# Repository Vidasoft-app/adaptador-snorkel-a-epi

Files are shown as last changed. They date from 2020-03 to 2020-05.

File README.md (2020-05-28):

# Adaptador máscara Snorkel a EPIs y CPAP

Ver en [Español](https://github.com/Vidasoft-app/mascaras-3d-coronavirus-protocas3d/blob/master/README.md), [English](https://github.com/Vidasoft-app/mascaras-3d-coronavirus-protocas3d/blob/master/README-en-gb.md).

[Entra en la página web oficial](https://coronavirus.vidasoft.es)

Proyecto de código abierto, libre para uso de la emergencia sanitaria.

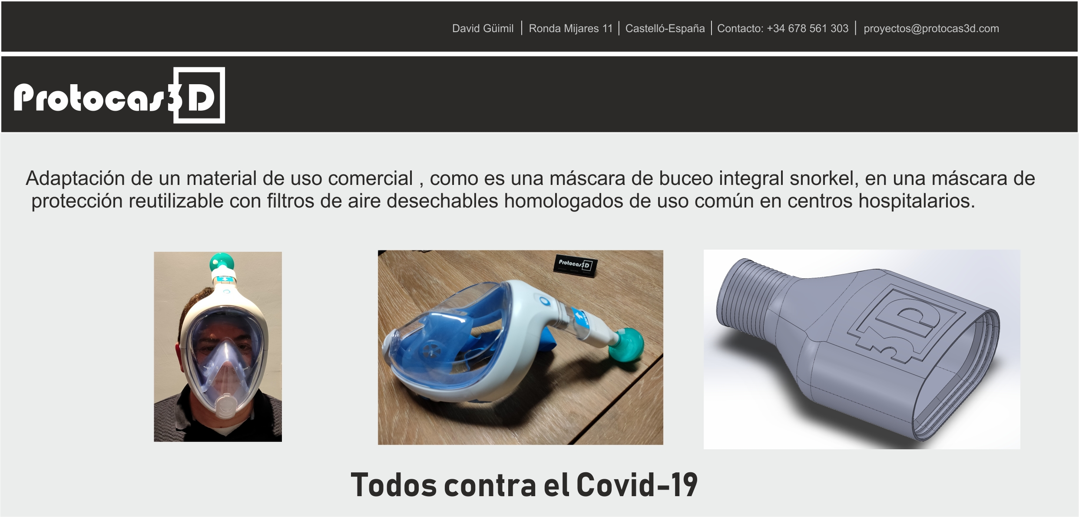
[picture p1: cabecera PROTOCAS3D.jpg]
imagen explicativa adaptación máscara buceo snorkel a EPIs sanitario


## ¿De que trata este proyecto?

Se trata de un adaptador para hacer compatible las máscaras de [snorkel](https://es.wikipedia.org/wiki/Esn%C3%B3rquel) con el filtro respiratorio hospitalario de forma que puedas usar la máscara de Snorkel de 2 maneras:

1. EPIs sanitario. Protección individual más completa y aislante.
2. Máscara para respirador (con CPAP) para uso no invasivo.

Estas piezas para EPIs o CPAP se puede crear mediante impresión 3D o mediante mecanizado industrial. 

Por otro lado, también se incluye para impresión 3D el emboltorio del "insumo desechable con filtro HEPA-H13" pero modificado para ser reutilizable. Sabemos que hay sitios dónde estos insumos desechables son un problema y tener esa pieza reutilizable puede ayudar.

Este adaptador te permite con unos sencillos pasos (más abajo) hacer que estas máscaras pueda ayudar como EPIs.

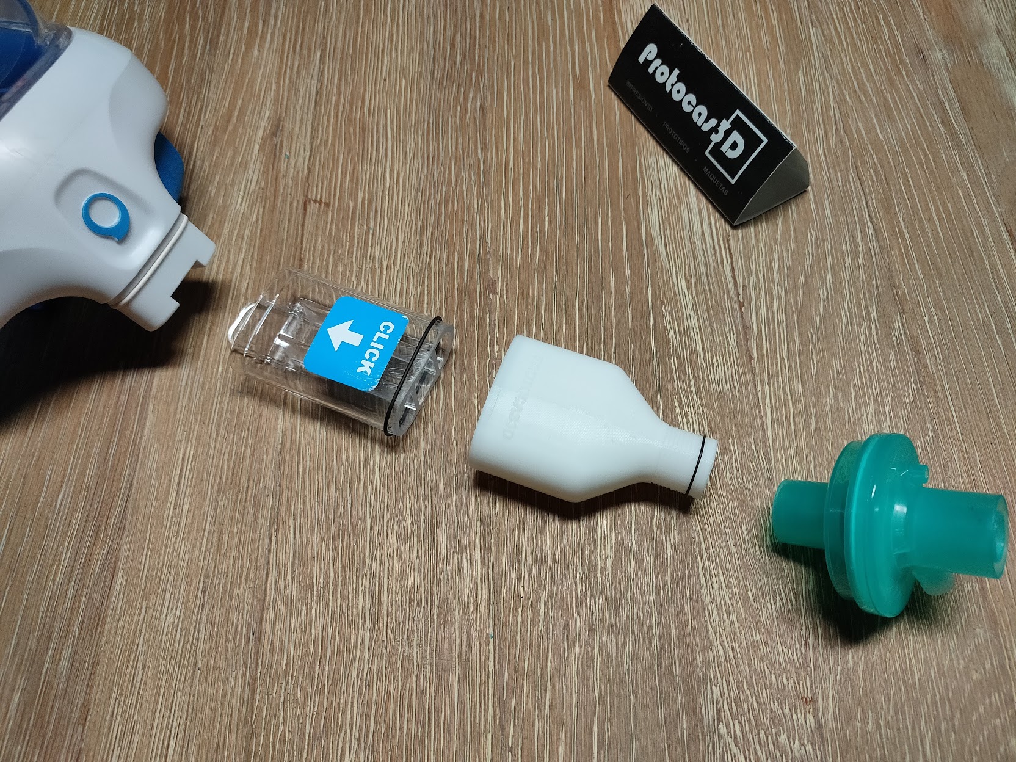
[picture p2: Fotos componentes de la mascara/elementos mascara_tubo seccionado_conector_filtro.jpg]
Máscara snorkel adaptada para ser EPI

Versión protección EPIs.

## Requisitos de impresión

* Impresión sin soportes.
* Extrusor 0,4 (que es el estándar)
* Temperatura extrusor 210
* Cama 50
* Material PLA (es el que utilizamos nosotros)

## Máscaras compatibles

* https://www.pccomponentes.com/ksix-mascara-snorkel-para-go-pro-y-camaras-deportivas
* https://www.decathlon.es/es/p/mascara-snorkel-ensuperficie-easybreath-500-oyster/_/R-p-148873?mc=8491269&c=VERDE_AZUL+TURQUESA
* https://www.decathlon.es/es/p/mascara-de-snorkel-en-superficie-easybreath-azul/_/R-p-1616?mc=8526111&c=AZUL_AZUL+TURQUESA

## Enlaces directos a las piezas

* Adaptador EPIs protección individual: 
  * Versión impresión 3D: [Enlace a las marcas de máscaras compatibles](https://github.com/Vidasoft-app/adaptador-snorkel-a-epi/tree/master/M%C3%A1scara%20snorkel%20a%20EPI_IMPRESI%C3%93N%203D)
  * Versión Mecanizado: [Enlace a los ficheros](https://github.com/Vidasoft-app/adaptador-snorkel-a-epi/tree/master/M%C3%A1scara%20snorkel%20a%20EPI_MECANIZADO/m%C3%A1scara%20Decathlon)
* Adaptador CPAP respirador no invasivo:
  * Versión impresión 3D: [Enlace a las marcas de máscaras compatibles](https://github.com/Vidasoft-app/adaptador-snorkel-a-epi/tree/master/Mascara%20snorkel%20a%20CPAP_IMPRESI%C3%93N%203D)
  * Versión Mecanizado: [Enlace a los ficheros](https://github.com/Vidasoft-app/adaptador-snorkel-a-epi/tree/master/M%C3%A1scara%20snorkel%20a%20CPAP_MECANIZADO)
* Emboltorio filtro HEPA-H13: [Enlace a los ficheros]()
  * Versión impresión 3D: [Enlace a los ficheros](https://github.com/Vidasoft-app/adaptador-snorkel-a-epi/tree/master/Filtro%20re-utilizable%20para%20EPI%20(PPE)_)

### ¿El adaptador no es compatible con tu máscara?

Tienes las fuentes disponibles [pulsando aquí](https://github.com/Vidasoft-app/adaptador-snorkel-a-epi/tree/master/Archivos%203D%20editables%20conector%20a%20filtro%20Version%204) para que puedas adaptarlo a tus necesidades estes dónde estes.

Código libre, ya sabes :)

## Proceso de adaptación

Los pasos son: 
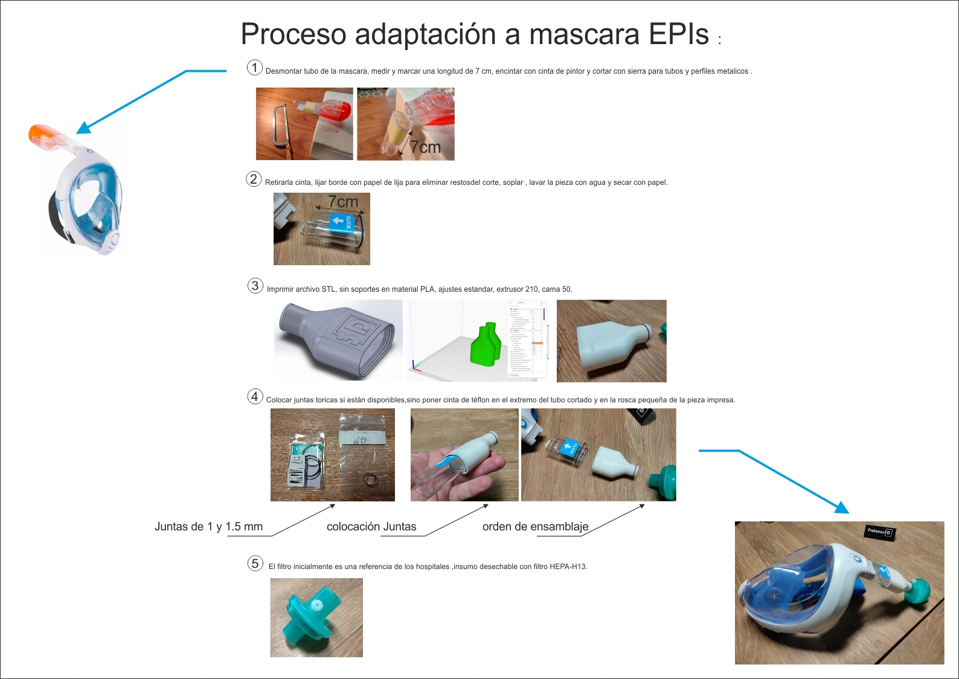
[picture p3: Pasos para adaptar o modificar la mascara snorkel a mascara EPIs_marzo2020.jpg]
Proceso de adaptación


También te los puedes descargar en PDF [pulsando en este enlace](https://github.com/Vidasoft-app/mascaras-3d-coronavirus-protocas3d/blob/master/Pasos%20para%20adaptar%20o%20modificar%20la%20mascara%20snorkel%20a%20mascara%20EPIs_marzo2020.pdf)

## ¿Como ponerse la máscara correctamente?

Te lo explicamos en [este vídeo](https://www.youtube.com/watch?v=PjzaguY-Ay0)

## ¿Tenemos licencia para tener este proyecto de código libre?

Si. El proyecto parte de unos médicos Colombianos los cuales nos han dado licencia explicita para compartir.

## ¿Tienes dudas? puedes preguntarnos directamente.

Puedes ponerte en contacto con todo el equipo del proyecto mediante el correo de:

coronavirus@vidasoft.es

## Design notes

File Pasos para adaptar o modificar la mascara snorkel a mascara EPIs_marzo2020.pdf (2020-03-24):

# Proceso adaptación a mascara EPIs :

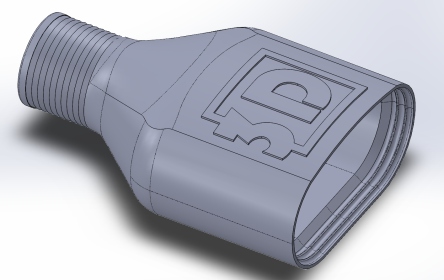
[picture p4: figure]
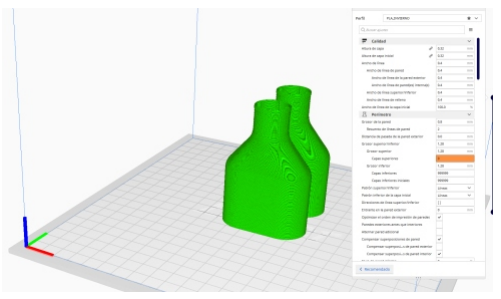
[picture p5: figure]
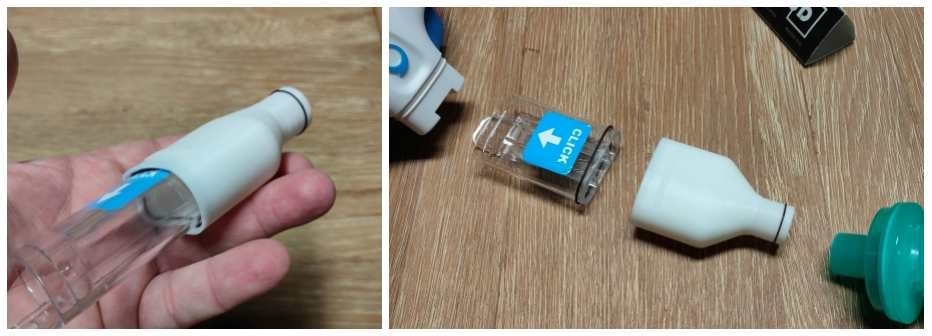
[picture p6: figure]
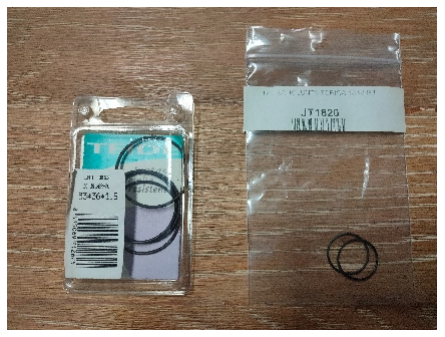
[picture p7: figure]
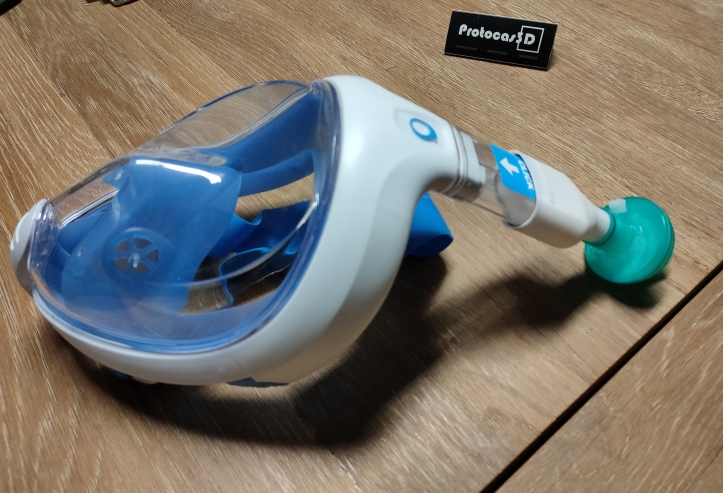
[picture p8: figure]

Juntas de 1 y 1.5 mm | colocación Juntas | orden de ensamblaje

Desmontar tubo de la mascara, medir y marcar una longitud de 7 cm, encintar con cinta de pintor y cortar con sierra para tubos y perfiles metalicos .

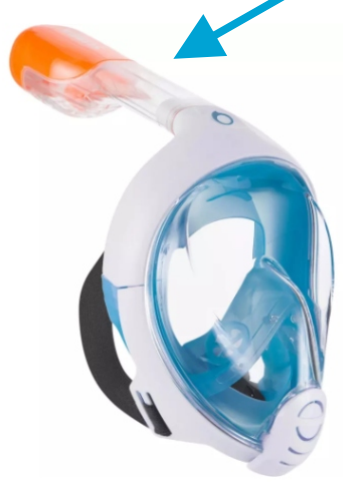
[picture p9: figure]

Retirarla cinta, lijar borde con papel de lija para eliminar restosdel corte, soplar , lavar la pieza con agua y secar con papel.

Imprimir archivo STL, sin soportes en material PLA, ajustes estandar, extrusor 210, cama 50.

Colocar juntas toricas si están disponibles,sino poner cinta de téflon en el extremo del tubo cortado y en la rosca pequeña de la pieza impresa.

El filtro inicialmente es una referencia de los hospitales ,insumo desechable con filtro HEPA-H13.

1

2

3

4

5

7cm

7cm

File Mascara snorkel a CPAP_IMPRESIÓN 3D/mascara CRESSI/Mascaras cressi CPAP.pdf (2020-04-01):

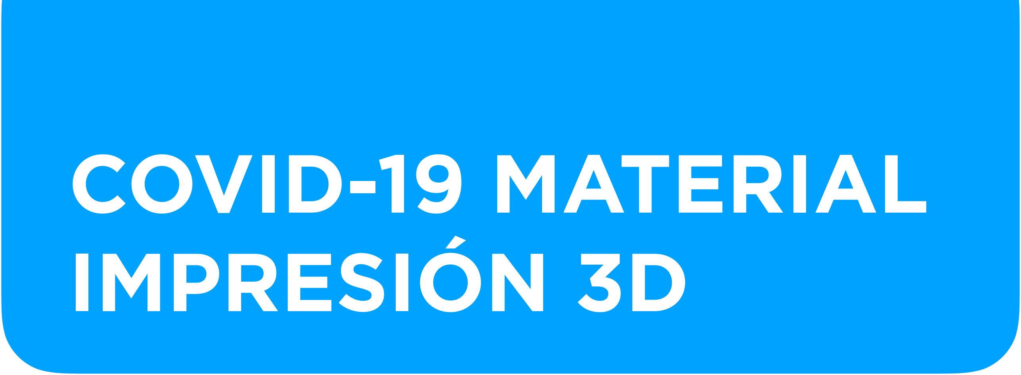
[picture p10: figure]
COVID-19 MATERIAL IMPRESIÓN 3D

# REFERENCIA: 3DPT021

USO

Adaptación de la máscara Duke de Cressi® para su uso como sistema CPAP de Boussignac

NECESIDAD

Se prevé aumento de la necesidad en todos los hospitales, debido a la alta previsión de pacientes que requerirán sistemas de respiración no invasivos en el pico de la epidemia.

# PARTES

1 | 3DPT021-1
Adaptador de la máscara Duke de Cressi®

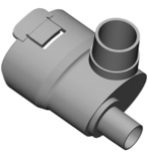
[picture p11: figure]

2 | 3DPT021-2

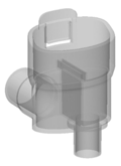
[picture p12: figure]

Soporte para válvula antiretorno

3 | 3DPT24

Opcional (en caso de no tener disponibilidad de filtro viricobacteriano)

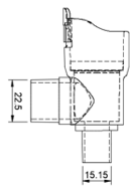
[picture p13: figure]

VALIDACIÓN CLINICA

- Máscara M/L i S/M Duke de Cressi®
- 3DPT021-1
- 3DPT021-2 ensamblada con la válvula

antirretorno de silicona extra, suministrada por el fabricante en el envase precintado de la misma máscara. En el interior de esta.

Resultados:

1. Con válvula antiretorno.
Se consiguieron presiones en el circuito a final de espiración de 10 cm H2O. No se observó la presencia de flujo retrógrado en todas las pruebas.

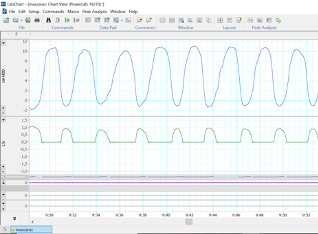
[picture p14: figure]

Resultados:

2. Sin Válvula antirretorno

Las presiones a final de espiración conseguidas alcanzaron 4 cm H2O (6 cm H2O inferiores a las esperadas). Asimismo, se detectó un incremento del flujo retrógrado atribuible a la ausencia de la válvula antiretorno extra.

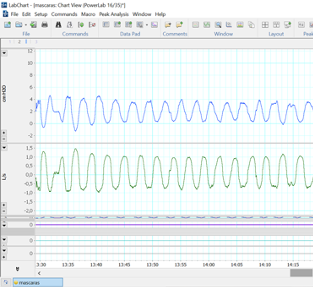
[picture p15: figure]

VALIDACIÓN IMPRESIÓN
La utilidad clínica de esta pieza ha sido validada en el Parc Taulí para FDM Biocompatible para producto sanitario Clase I

OPCIONES DE IMPRESIÓN:

- Material: material rígido
- Tecnología: FDM o SLA. Se descarta SLS por posible entrada de polvo en el paciente.

1 2

## INSTRUCCIONES DE MONTAJE

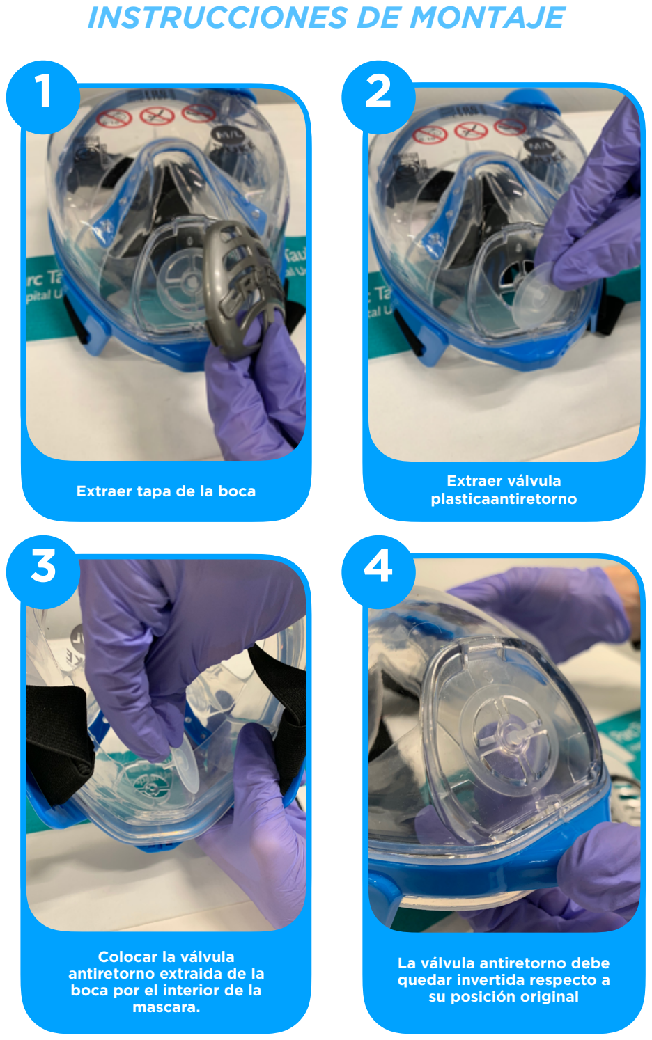
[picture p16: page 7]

3 4

Extraer tapa de la boca | Extraer válvula plasticaantiretorno

Colocar la válvula
antiretorno extraida de la boca por el interior de la mascara.

La válvula antiretorno debe quedar invertida respecto a su posición original

5 6

## INSTRUCCIONES DE MONTAJE

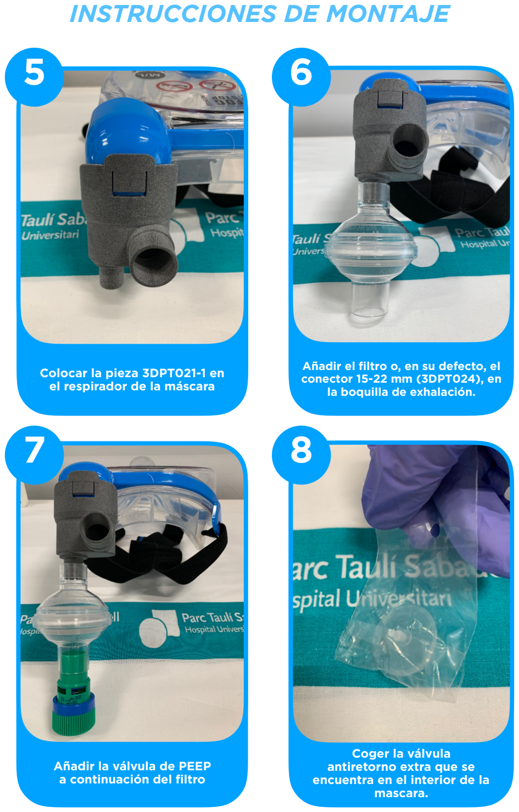
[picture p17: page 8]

7 8

Colocar la pieza 3DPT021-1 en el respirador de la máscara

Añadir el filtro o, en su defecto, el conector 15-22 mm (3DPT024), en la boquilla de exhalación.

Añadir la válvula de PEEP
a continuación del filtro

Coger la válvula
antiretorno extra que se
encuentra en el interior de la mascara.

9 10

## INSTRUCCIONES DE MONTAJE

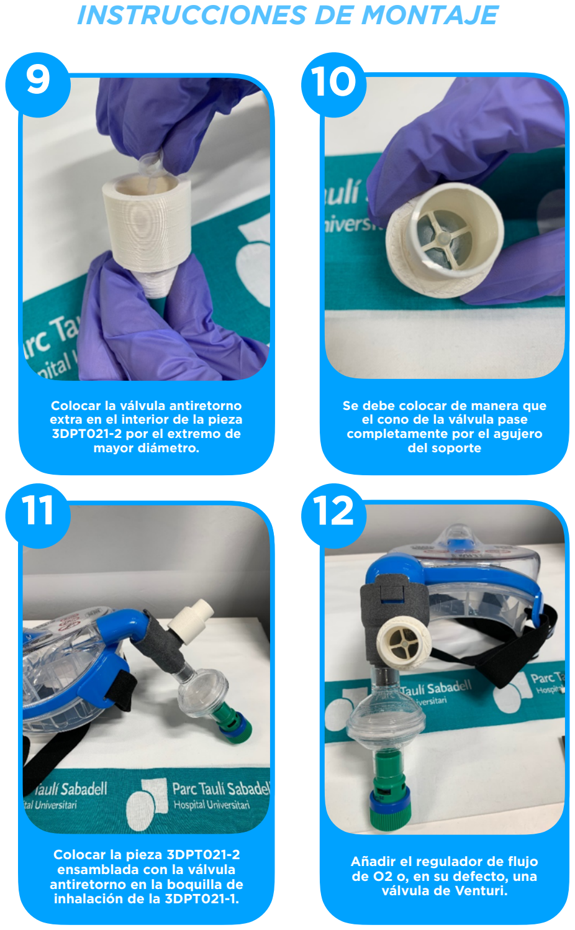
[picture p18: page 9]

11 12

Colocar la válvula antiretorno extra en el interior de la pieza 3DPT021-2 por el extremo de mayor diámetro.

Se debe colocar de manera que el cono de la válvula pase completamente por el agujero del soporte

Colocar la pieza 3DPT021-2 ensamblada con la válvula
antiretorno en la boquilla de inhalación de la 3DPT021-1.

Añadir el regulador de flujo de O2 o, en su defecto, una válvula de Venturi.

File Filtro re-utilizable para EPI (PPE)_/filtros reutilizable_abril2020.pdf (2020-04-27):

## Filtro reutilizable para EPI (PPE)

1

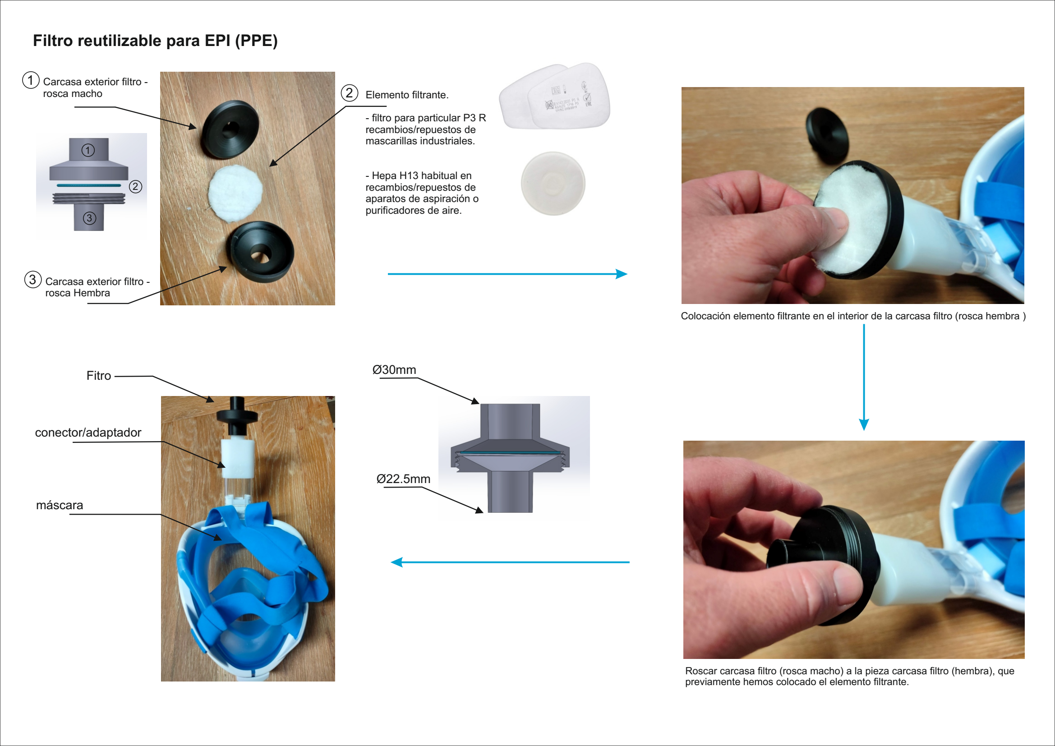
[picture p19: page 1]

### Ø30mm

### Ø22.5mm

### Fitro

### conector/adaptador

### máscara

Carcasa exterior filtro -
rosca macho

Carcasa exterior filtro -
rosca Hembra

3

Elemento filtrante.

- filtro para particular P3 R
- Hepa H13 habitual en
recambios/repuestos de
aparatos de aspiración o
purificadores de aire.

recambios/repuestos de
mascarillas industriales.

Colocación elemento filtrante en el interior de la carcasa filtro (rosca hembra )

Roscar carcasa filtro (rosca macho) a la pieza carcasa filtro (hembra), que previamente hemos colocado el elemento filtrante.

2

1

2

3

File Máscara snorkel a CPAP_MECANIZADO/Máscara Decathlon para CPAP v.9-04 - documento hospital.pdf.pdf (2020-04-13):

Hospital General Universitari de Castelló Medicina Intensiva

Avgda. Benicàssim, s/n 12004 Castelló - Tel. (+34) 964 725 000 - www.castello.san.gva.es | página 1 de 10

# Máscara para CPAP

Se han adaptado máscaras de snorkel de la marca decathlon para ser utilizada para CPAP conectada a diversas fuentes de entrada de gases y con diversos tipos de válvulas.

Su empleo puede tener beneficios terapéuticos, pero precisa de un correcto montaje y es necesaria la monitorización estrecha de los pacientes más graves.

El sistema descrito NO SE HA PROBADO para Ventilación No Invasiva. Sólo para CPAP

Es IMPORTANTE distinguirla de otra adaptación diferente y que se utiliza como alternativa a las gafas/pantalla + mascarilla de EPI (ver foto de la máscara EPI en última página).

FUNCIONAMIENTO
La máscara se adapta a la cara del paciente y en la parte superior tiene una pieza (verde) con dos bocas que pueden intercambiarse. A una de ellas se conecta una fuente de gas a alto flujo (al menos 30 L/min) y a la otra una válvula de PEEP que es la que define la presión mínima dentro de la máscara y por lo tanto en la vía aérea.

COMPONENTES: Tres

1º) Máscara decathlon con pieza de verde enchufada.

2º) Circuito de suministro de gas (circuito inspiratorio).
Cuatro opciones:
1) Caudalímetros para gafas nasales de alto flujo conectados a tubuladura respirador
2) Caudalímetro de alto flujo de O2 para CPAP (Venturi, muy ruidoso) conectado a tubuladura respirador
3) Caudalímetros de pared en paralelo (se pueden incluir hasta 3) conectados a través de adaptador blanco a tubuladura respirador.
4) Airvo-2 conectado a tubuladura de respirador
Opción todavía no probada: Ventilador V60 o Vision en modo CPAP y tubuladura de una rama.

3º) Circuito espiratorio: consta de filtro HEPA y válvula de PEEP

Avgda. Benicàssim, s/n 12004 Castelló - Tel. (+34) 964 725 000 - www.castello.san.gva.es | página 2 de 10

### COMPONENTES

CIRCUITO DE SUMINISTRO DE GAS (CIRCUITO INSPIRATORIO): Varias opciones

1) Caudalímetros: La forma más simple es un mezclador como el de las gafas nasales de alto flujo.
- Como alternativa al mezclador de las gafas nasales de alto flujo se ha desarrollado un adaptador que mezcla gases de caudalímetros convencionales (aire medicinal y O2) y tiene un diámetro de salida que conecta a tubuladuras de respirador.
- NO deben colocarse cámaras de burbujeo en los caudalímetros, sino conectar los tubos directamente.
- Disponemos de algunos caudalímetros de alto flujo (los de CPAP, no Boussignac) capaces de suministrar 30L/min. Esperamos disponer de mas caudalímetros de alto flujo, pero actualmente hay escasez. Los habituales dispensan un flujo de hasta 15 L.
- Existe la posibilidad de combinar un caudalímetro doble de O2 (= 2 x 15 L) en la misma toma de O2 (con una toma doble de pared) + una de aire de 15 L. El inconveniente es que dispensa una FiO2 muy elevada.
- Para conocer la FiO2 administrada el método aproximado es utilizar tablas. La alternativa es un medidor de FiO2 intercalado en el tubo que llega al paciente, pero estamos escasos.
2) NO se pueden utilizar sistemas basados en Venturi (como Ventimask o similares) porque la CPAP impide su funcionamiento y sólo se consigue fugar O2 al entorno.
3) Airvo-2: versión sofisticada de las GNAF que incorpora la posibilidad de humidificación activa. Esperamos tener (mayo). Hay alguno en Neumología

BALÓN RESERVORIO:
Una forma visual de comprobar la adecuación del flujo de gas se basa en añadir un balón reservorio en T en la tubuladura que va hacia el paciente. Si el balón se colapsa en la inspiración significa que el flujo es suficiente. Si se mantiene muy hinchado durante todo el ciclo respiratorio significa que el flujo de gas es excesivo.

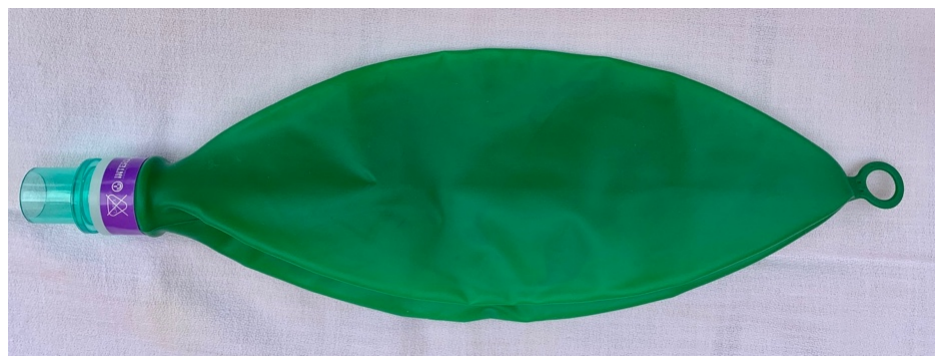
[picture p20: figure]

Avgda. Benicàssim, s/n 12004 Castelló - Tel. (+34) 964 725 000 - www.castello.san.gva.es | página 3 de 10

Es opcional.

HUMIDIFICACIÓN:
- Para la humidificación de la mezcla de inspiratoria debe intentarse que el paciente respire por vía nasal.
- En pacientes con altos requerimientos de FiO2 puede ser conveniente acoplar humidificación activa (humificador con calentador) en el circuito inspiratorio, cerca del paciente y siempre después del filtro HEPA inspiratorio. Ello favorecerá la fluidificación de las secreciones pero favorecerá la condensación de H2O en el circuito (con obstrucción parcial del flujo), máscara (con visión dificultada), filtro HEPA espiratorio y válvula PEEP que pueden disfuncionar. Es por tanto opcional.

VÁLVULA DE PEEP
Es importante tener en cuenta que la presión al final de la espiración en la vía aérea del paciente puede ser superior a la presión de apertura de la válvula de PEEP, pues el alto flujo de gas necesario ejerce también cierto nivel de presión. Por ello es aconsejable iniciar con válvulas de PEEP baja para comprobar la tolerancia del paciente, e ir incrementando posteriormente. TIPOS de válvula
1. No regulable: Tiene una PEEP nominal establecida, visible en el exterior de la válvula, así como una flecha que indica la dirección en que debe circular el gas. Dependiendo del fabricante el diámetro de la boca de entrada es diferente y el conector a utilizar para unirlo al filtro HEPA es diferente.

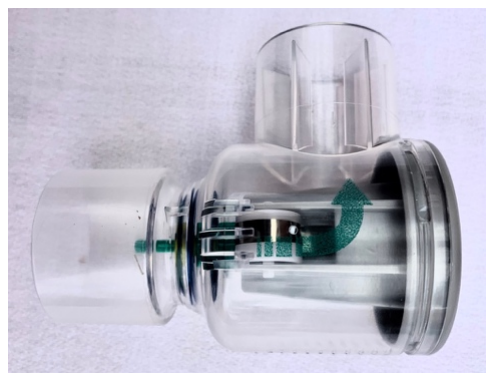
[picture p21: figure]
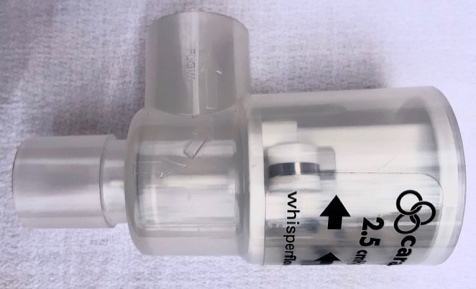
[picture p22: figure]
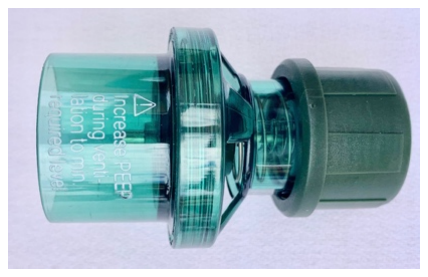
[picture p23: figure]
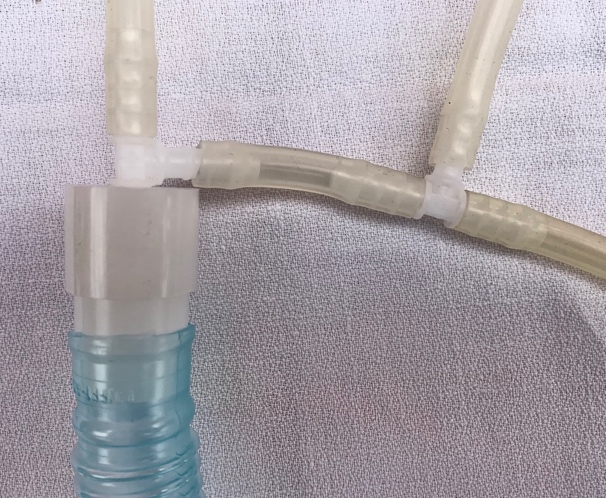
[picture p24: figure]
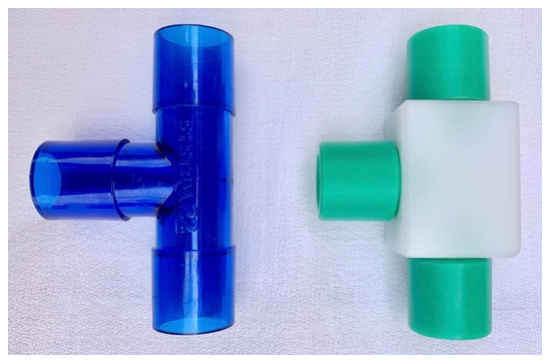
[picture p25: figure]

Avgda. Benicàssim, s/n 12004 Castelló - Tel. (+34) 964 725 000 - www.castello.san.gva.es | página 4 de 10
2. Regulable: Son las válvulas del Ambú, y se regulan girando la rueda final llegando hasta 20 cmH2O. Sólo tiene un punto para conectar al filtro HME.
No tienen boca de salida.

Importante: si está cerrada del todo la rosca reguladora produce la máxima PEEP. Iniciar con rosca aflojada a tope

CONECTORES
1. Pieza de conexión de caudalímetros a tubo de
circuito de ventilador. Vienen preparado con 3 entradas para 3 caudalímetros. En caso de ser sólo 2 deberá desmontarse una de las T (y guardarse).
2. Pieza en T que se intercala en el tubo que lleva gas al paciente. En la otra boca se puede conectar el balón reservorio o un medidor de FiO2. En la imagen las tres bocas de la T son del mismo calibre, pero las hay de diferente calibre Disponemos de modelos de varios fabricantes y su color varía.

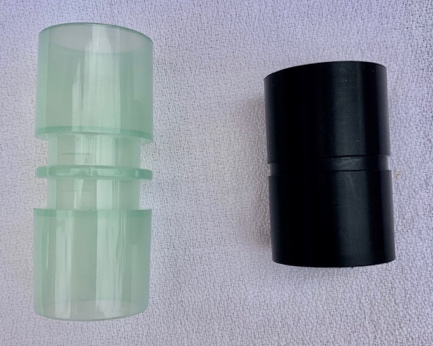
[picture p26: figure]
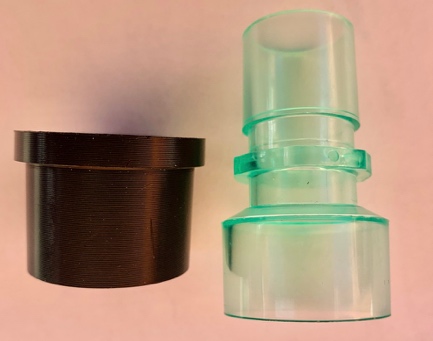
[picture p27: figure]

Avgda. Benicàssim, s/n 12004 Castelló - Tel. (+34) 964 725 000 - www.castello.san.gva.es | página 5 de 10
3. Conector recto de calibre estándar con 2 bocas iguales. Se utiliza para conectar filtro HME con pieza verde de la máscara en algunos casos, o para conectar algunos tipos de válvula de PEEP no desechable al filtro HME. Disponemos de modelos de varios fabricantes y su color varía.
4. Conector recto de calibre ancho. Sirve para conectar algunos modelos de las válvulas de PEEP (las regulables y alguno de los modelos no regulables) a la porción final del circuito. Disponemos de modelos de varios fabricantes y su color varía.


Avgda. Benicàssim, s/n 12004 Castelló - Tel. (+34) 964 725 000 - www.castello.san.gva.es | página 6 de 10

MÁSCARA:

Hay varios tamaños dependiendo del paciente. Es importante que ajuste bien a la cara para que no haya fugas.

- La máscara ya ha sido modificada y es diferente a la versión comercial. Tiene una válvula en la zona del mentón que ha sido invertida para que se abra sólo en inspiración e impida la espiración.
- Hay otras dos válvulas en que separan el compartimento nasobucal del compartimento que abarca ojos y resto de la cara. Esas dos válvulas no tienen un comportamiento crítico. Si están colocadas en sentido de impedir el paso de gas al compartimento oculo-facial (por defecto), se asegura mejor la máscara y se minimizan las fugas. El inconveniente es que puede haber condensación en la zona de visión. Si eso supone un factor de disconfort importante se pueden quitar tirando de ellas con cuidado (y guardarlas).
- La máscara ya lleva acoplada en su parte superior la pieza verde con 2 bocas de conexión
- NO SE DEBE HACER NINGUNA OTRA MODIFICACIÓN


Avgda. Benicàssim, s/n 12004 Castelló - Tel. (+34) 964 725 000 - www.castello.san.gva.es | página 7 de 10

CIRCUITO ESPIRATORIO:

Consta de:
1) Filtro HEPA conectado directamente a la pieza verde de la máscara. En caso de aplicar humidificación activa es importante cambiarlo cada 8 h pues al saturarse de humedad aumenta la resistencia al flujo hasta niveles críticos.
2) Válvula de PEEP. Es la última pieza del circuito y por tanto el punto de salida a la atmósfera

MONTAJE:
1. Circuito inspiratorio: conectar fuente de gas mediante tubuladura desechable a una de las bocas de la pieza verde de la máscara. En la parte proximal (cerca de caudalímetros o del ventilador) debe incluir un filtro HEPA.
2. Como opciones el circuito de aporte de fuente de gas inspiratorio puede incluir tras el filtro HEPA
a. Balón reservorio en T
b. Humidificación activa
3. Conectar el circuito espiratorio a la otra boca de la pieza verde de la máscara. Consta de filtro HPA espiratorio y a continuación una válvula de PEEP en el sentido correcto. La válvula es el final del circuito, por donde saldrá gas espirado mezclado con el excedente del gas suministrado hacia la atmósfera.


Avgda. Benicàssim, s/n 12004 Castelló - Tel. (+34) 964 725 000 - www.castello.san.gva.es | página 8 de 10

RECAMBIO DE FILTROS HEPA
- Cada 5 días
- En caso de humidificación activa se cambiará el HEPA espiratorio cada 8 horas o antes si se sospecha obstrucción

Ejemplo de circuito con conexión a tres caudalímetros y balón


Avgda. Benicàssim, s/n 12004 Castelló - Tel. (+34) 964 725 000 - www.castello.san.gva.es | página 9 de 10

COLOCACIÓN
- Separar con ambas manos las gomas de sujeción e introducir la cabeza por la abertura inferior.
- Ajustar bien la zona de boca-nariz
- Asegurar que la fuente de gas está en marcha y con flujo adecuado
- Instar al paciente a respirar lentamente y por la nariz. Inicialmente puede crear algo de agobio por lo que hay que quedarse al lado del paciente unos minutos hasta comprobar el buen funcionamiento del sistema y su confort.
- Hay que asegurar que el flujo de gas inspiratorio es adecuado. Una forma visual de valorarlo es intercalando un balón reservorio en el circuito inspiratorio

DISPONIBILIDAD
- Ya tenemos material para su montaje.
- Ya están modificada su válvula principal y con la pieza verde colocada.

PROCESADO TRAS LA RETIRADA
Todos los componentes se reutilizarán
- Los filtros HEPA inspiratorio y espiratorio se desecharán en una bolsa dedicada a recoger los filtros.
- La máscara junto a la pieza verde sin desmontar se procesará en otro circuito para poder ser reutilizada. El empleo de soluciones líquidas implica que se precisan horas para el secado de las gomas de sujeción.
- Las válvulas de PEEP se lavarán y reutilizarán
- El balón se lavará
- Todo el resto de conectores también se lavarán y guardarán para su reutilización


Avgda. Benicàssim, s/n 12004 Castelló - Tel. (+34) 964 725 000 - www.castello.san.gva.es | página 10 de 10

### MÁSCARA DECATHLON PARA EPI

El aspecto es similar al de la máscara para CPAP pero no cuenta con la pieza verde en la parte superior. En su lugar tiene una pieza, en esta foto negra (pero las hay de diversos colores), de una sola vía y sus válvulas no han sido modificadas.

NO PUEDEN ser utilizadas para CPAP.

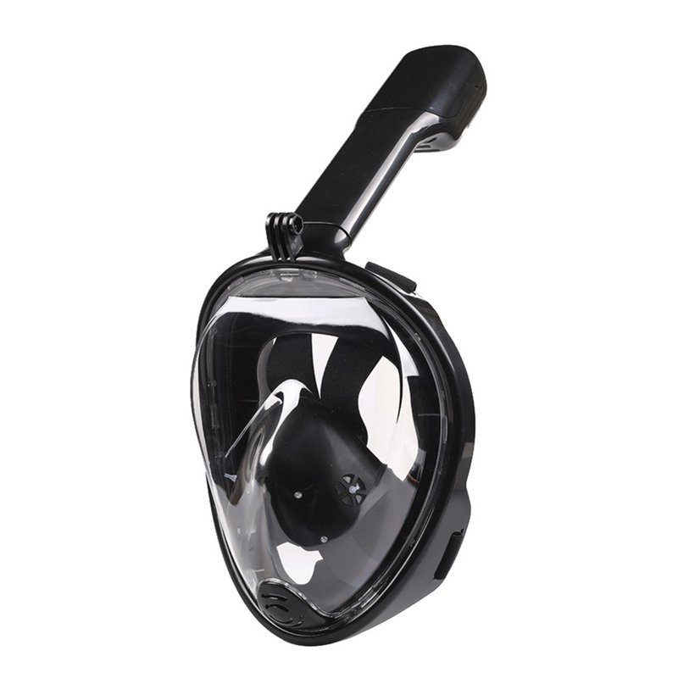
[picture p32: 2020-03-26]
docs/assets/images/snorkel_ksix-big.jpg

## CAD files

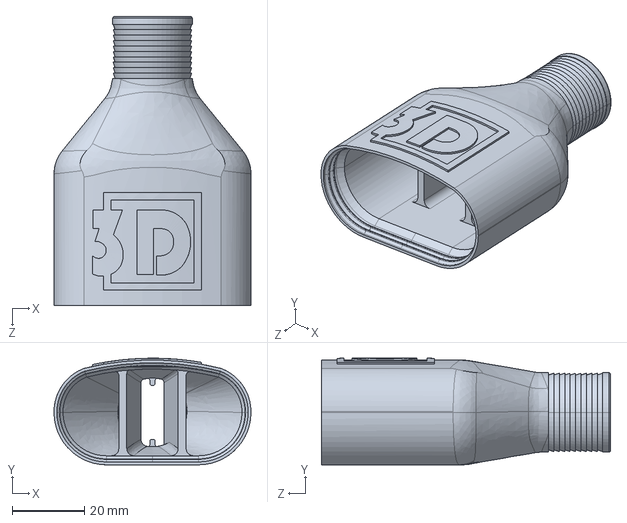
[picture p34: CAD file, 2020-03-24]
Archivos 3D editables conector a filtro Version 4/conector a filtro_v4.STEP
54.5 x 29.5 x 80.0 mm

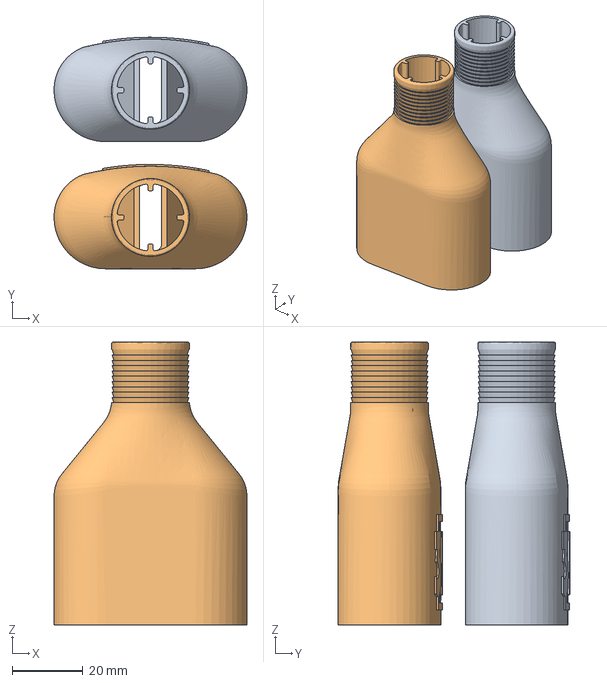
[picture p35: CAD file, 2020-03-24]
ender 3/CE3_filtro_V4_2 unidades.3mf
54.5 x 65.5 x 80.0 mm

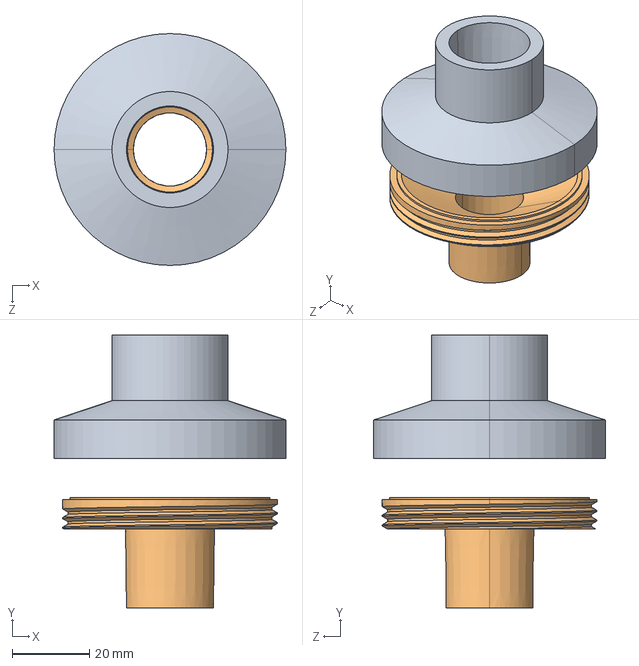
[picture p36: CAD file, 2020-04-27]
Filtro re-utilizable para EPI (PPE)_/DISEÑO EDITABLE/FILTRO_Ø50MM.STEP
60.0 x 70.6 x 60.0 mm

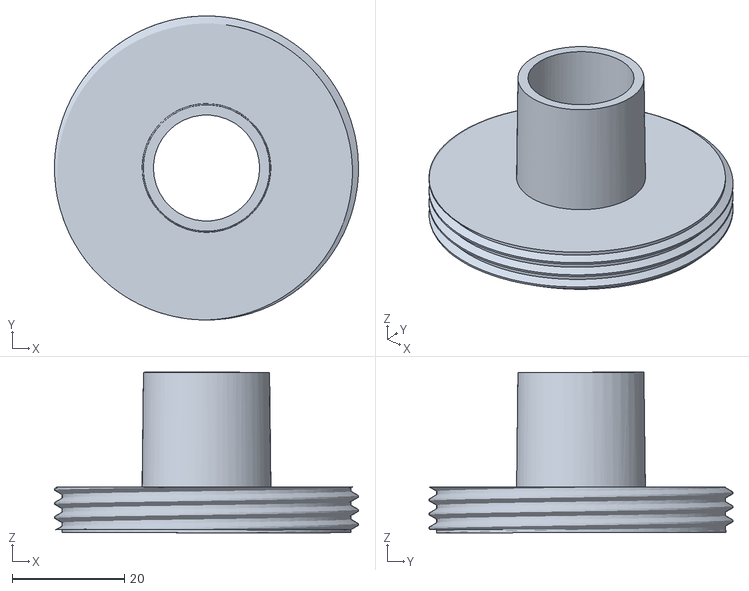
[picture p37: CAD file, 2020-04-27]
Filtro re-utilizable para EPI (PPE)_/FILTRO_macho_Ø50MM.stl
54.2 x 54.2 x 28.6

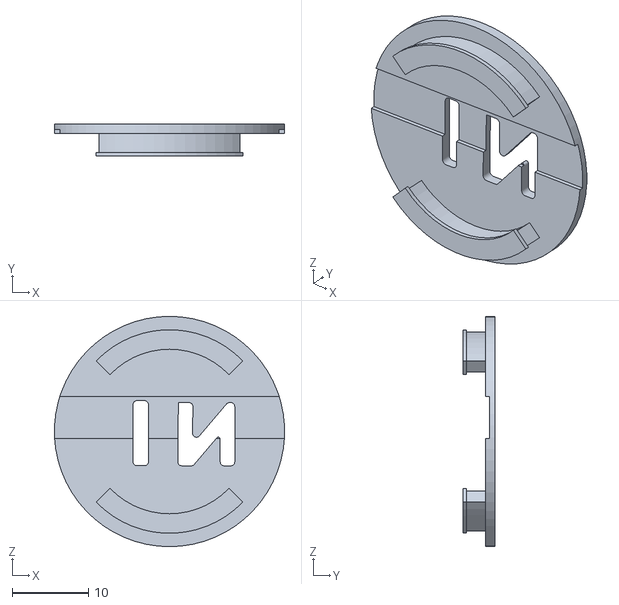
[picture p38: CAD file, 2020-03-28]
Mascara snorkel a CPAP_IMPRESIÓN 3D/mascara Decathlon/TAPA CPAP.STL
30.1 x 4.25 x 30.1

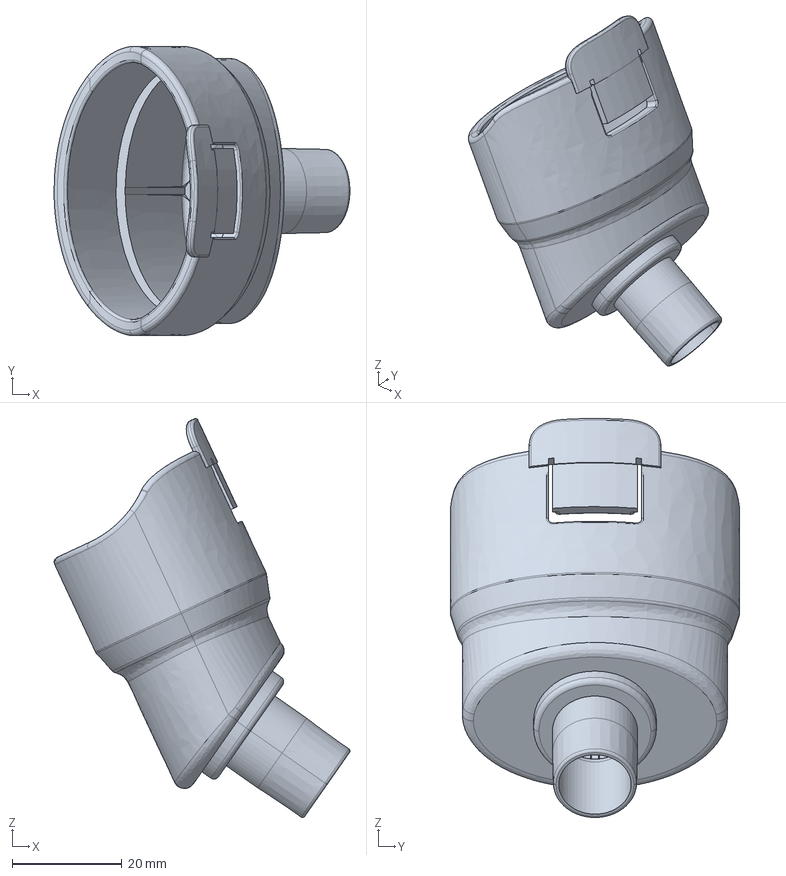
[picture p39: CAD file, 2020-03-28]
Máscara snorkel a EPI_IMPRESIÓN 3D/máscara Cressi/valvola_duke_filtroda15mm.stp
53.9 x 52.7 x 72.7 mm

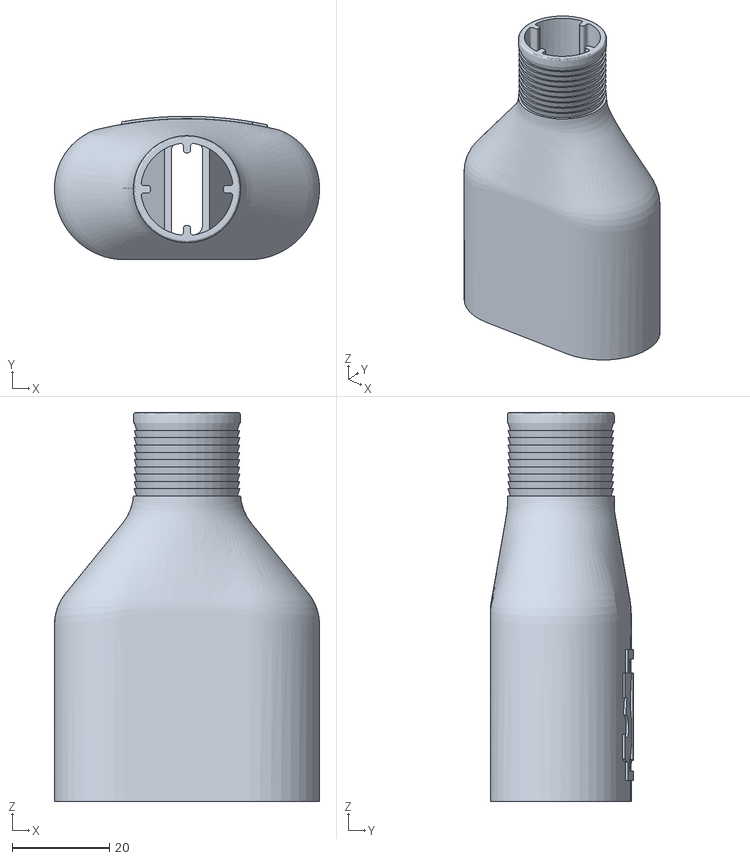
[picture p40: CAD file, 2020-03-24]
Máscara snorkel a EPI_IMPRESIÓN 3D/máscara Decathlon/conector filtro V4.STL
54.5 x 29.5 x 80.0

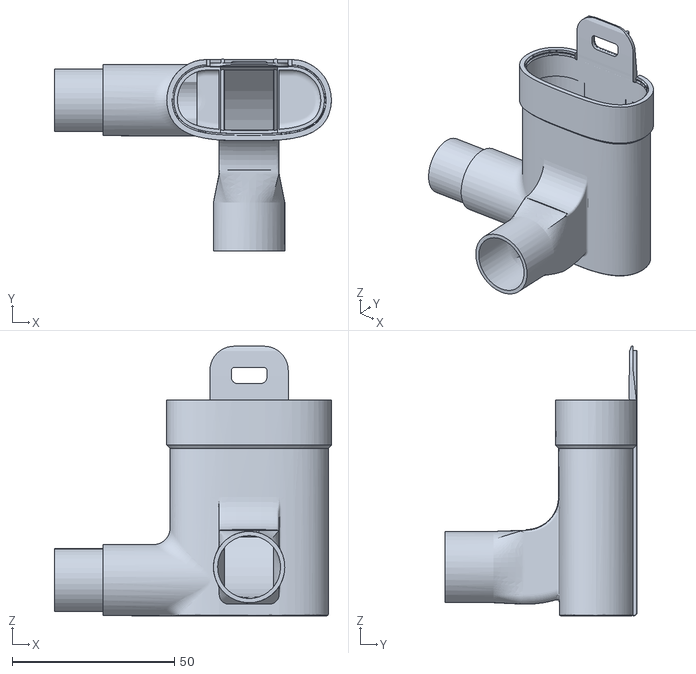
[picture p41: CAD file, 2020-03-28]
Snorkel CPAP/Mascara snorkel a CPAP_IMPRESIÓN 3D/mascara Decathlon/Charlotte Valve 1_CS_V3.stl
85.4 x 59.2 x 83.1

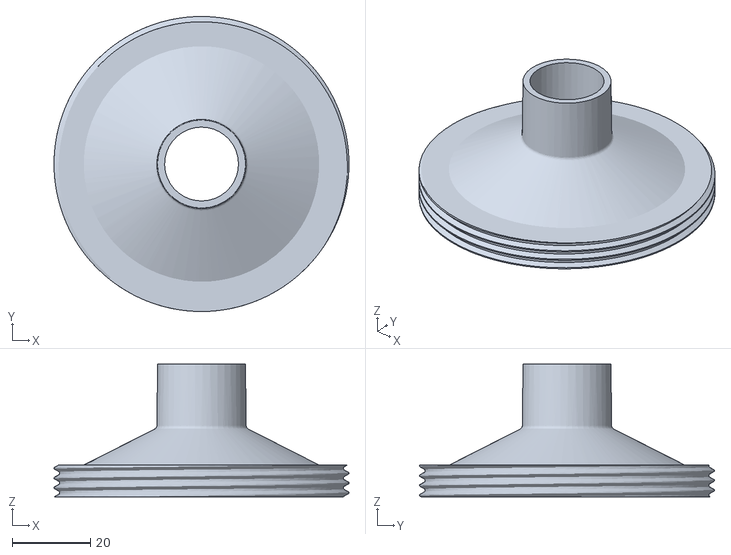
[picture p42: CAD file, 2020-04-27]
Filtro re-utilizable para EPI (PPE)_/FILTRO_macho_Ø75MM.stl
75.5 x 75.5 x 34.0

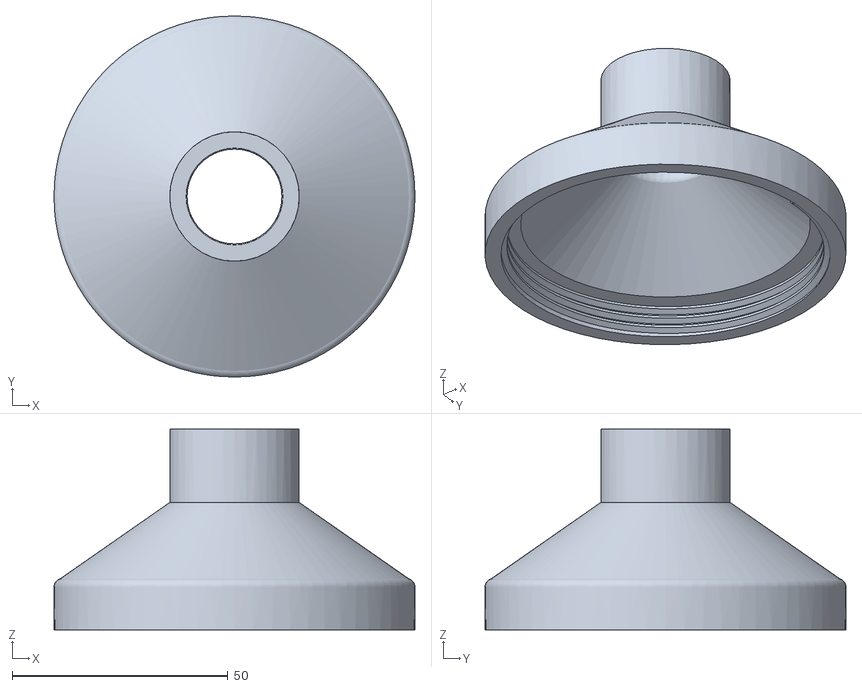
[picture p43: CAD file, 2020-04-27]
Filtro re-utilizable para EPI (PPE)_/FILTRO_Hembra_Ø75MM.stl
83.7 x 83.7 x 46.5

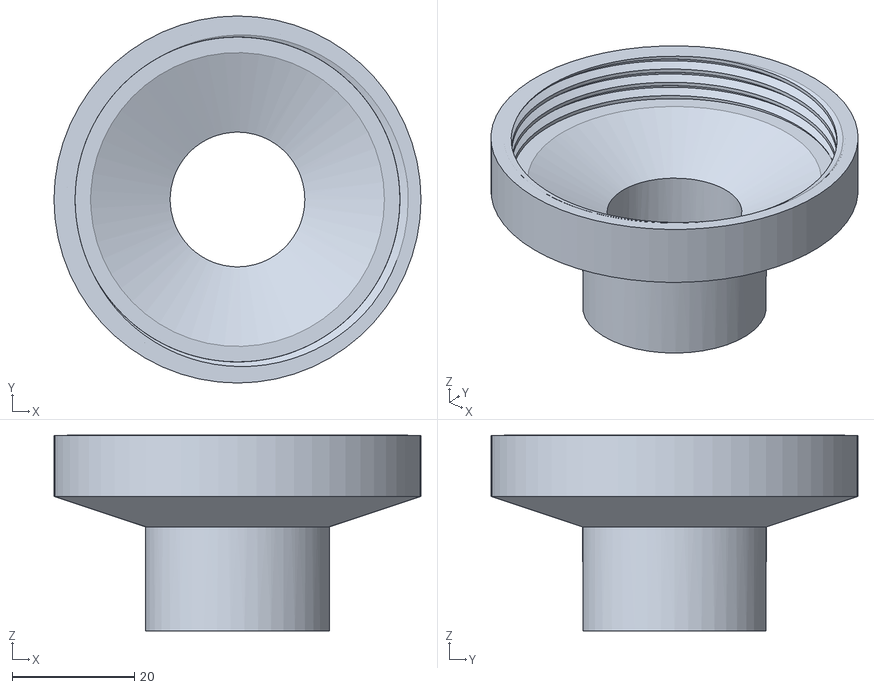
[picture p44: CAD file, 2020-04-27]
Filtro re-utilizable para EPI (PPE)_/FILTRO_Hembra_Ø50MM.stl
60.0 x 60.0 x 32.0

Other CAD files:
Archivos 3D editables conector a filtro Version 4/conector a filtro_v4.IGS
Archivos 3D editables conector a filtro Version 4/conector a filtro_v4.SLDDRW
Filtro re-utilizable para EPI (PPE)_/DISEÑO EDITABLE/FILTRO_Ø50MM.IGS
Máscara snorkel a EPI_IMPRESIÓN 3D/máscara Cressi/valvola_duke_filtroda15mm.STL

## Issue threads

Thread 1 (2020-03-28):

### ISSUE TITLE
Improving support requirements

### ISSUE THREAD

**Issue by jpmrodrigues** [Vidasoft-app/adaptador-snorkel-a-epi#1]
Hi,

First of all, thanks for the effort.

I'm trying to print this part but it has some support requirements that I think can be mitigated. Namely the guides on the top part could start with a 45º gradient.

Also, please remove the text since it takes time, needs support and only adds texture which is bad for particle retention.

Again, thanks :)

**Comment by Vidasoft-app** [comment]
Hi,

Thanks a lot for your comments.

I've shared the message with David. He is the one who knows about 3D printing and made the files.

He told me that the print is made without supports.

He also gave me more information about the printing specs:

* 0.4 Extrusor (it's the standard one)
* Extrusor temperature 210°C
* Bed 50
* PLA material (the one we use)

I have updated the README.md file to add these specs.

if you need to modify the font. You have the files available [here](https://github.com/Vidasoft-app/mascaras-3d-coronavirus-protocas3d/tree/master/Archivos%203D%20editables%20conector%20a%20filtro%20Version%204).

Thanks

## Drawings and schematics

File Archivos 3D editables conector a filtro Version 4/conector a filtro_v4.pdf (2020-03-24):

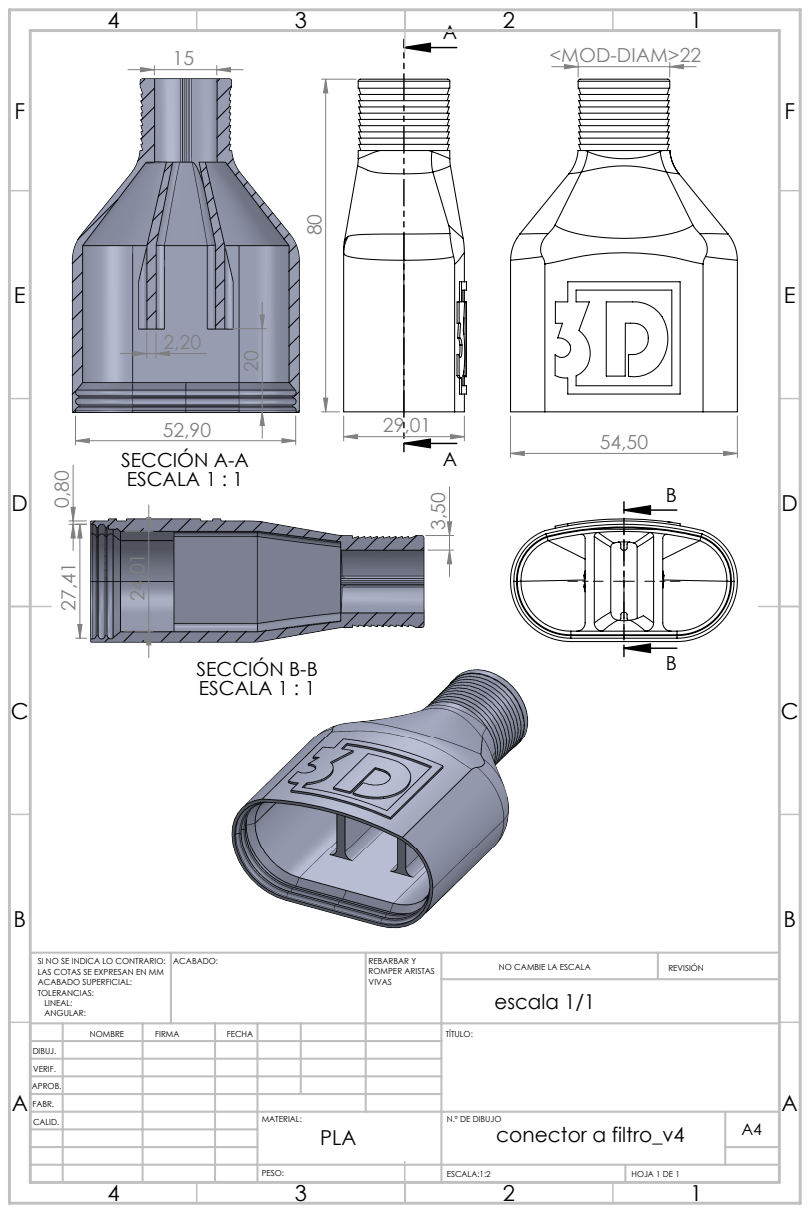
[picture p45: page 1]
SECCIÓN A-A ESCALA 1 : 1; SECCIÓN B-B ESCALA 1 : 1; ACABADO:; REBARBAR Y; ROMPER ARISTAS; NO CAMBIE LA ESCALA; REVISIÓN; ESCALA:1:2; HOJA 1 DE 1; escala 1/1

SI NO SE INDICA LO CONTRARIO:
LAS COTAS SE EXPRESAN EN MM
ACABADO SUPERFICIAL:
TOLERANCIAS:
LINEAL:
ANGULAR:

NOMBRE | FIRMA | FECHA | | | | TÍTULO:

DIBUJ.
VERIF.
APROB.
FABR.
CALID. | | | | MATERIAL: PLA | N.º DE DIBUJO conector a filtro_v4 | A4

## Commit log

2020-03-24 Ficheros proyecto
    [CE3_filtro_V4_2 unidades.3mf, conector a filtro_v4.IGS, conector a filtro_v4.SLDDRW, conector a filtro_v4.STEP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]
2020-03-25 Añadido requisitos de impresión
2020-03-26 Modificación página de inicio
2020-03-26 Cosas de diseño
2020-03-26 modificado index para poner imagenes del proyecto
2020-03-26 Añadidas descripciones de imagenes inicio
2020-03-26 modificaciones de textos
2020-03-26 Arreglada carga de imagenes
2020-03-27 añadido vídeo de como ponerse la máscara
2020-03-27 Actualizada mensaje de actualización
2020-03-28 Añadido colaborar que aporta máscaras Cressi España
2020-03-30 Mejorada la organización de ficheros
    [Adaptador Mascara-filtros.x_t, Charlotte Valve 1_CS_V3.stl, TAPA CPAP.STL, conector filtro V4.STL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]
2020-04-01 Solucionados errores menores
    [raccordo_Y.igs, raccordo_Y.stp, valvola_duke_24_3_2020.stp, valvola_duke_filtroda15mm.stp]
2020-04-02 Actualizadas fuentes
    [raccordo_Y.STL, raccordo_Y.igs, raccordo_Y.stp, valvola_duke_24_3_2020.STL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]
2020-04-27 Añadido filtro reutilizable
    [FILTRO_Hembra_Ø50MM.stl, FILTRO_Hembra_Ø75MM.stl, FILTRO_macho_Ø50MM.stl, FILTRO_macho_Ø75MM.stl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]
